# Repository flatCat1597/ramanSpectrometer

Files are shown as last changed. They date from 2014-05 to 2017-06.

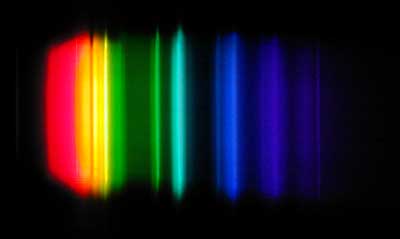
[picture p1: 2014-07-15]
info/images/youTube/video_1/images/Spectrum-hp-sodium.jpg

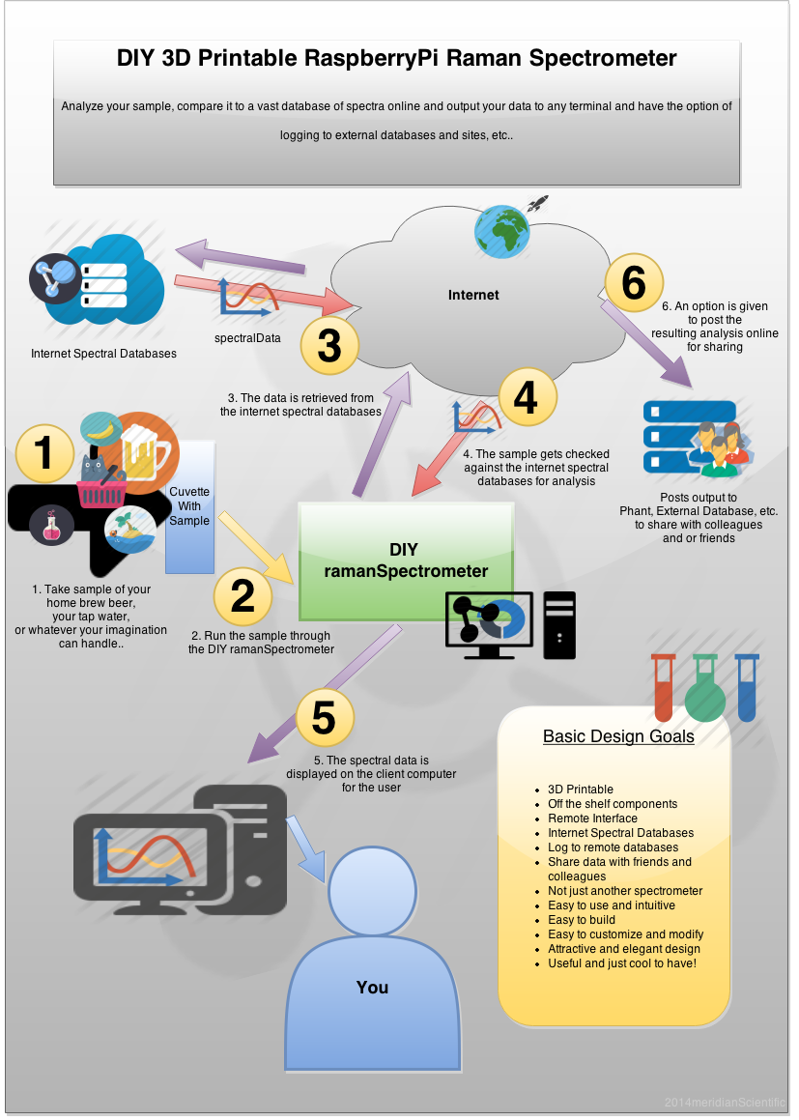
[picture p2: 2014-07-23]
info/images/diagrams/overview.png

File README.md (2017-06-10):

ramanPi
the DIY 3D Printable Raman Spectrometer

This repository will no longer contain ANY updates to the project.  The new repository at gitLab will have the latest files.  The github repo will NO LONGER be updated.  Please check the repository at https://gitlab.com/ramanPi before using any of the files here to build a ramanPi.

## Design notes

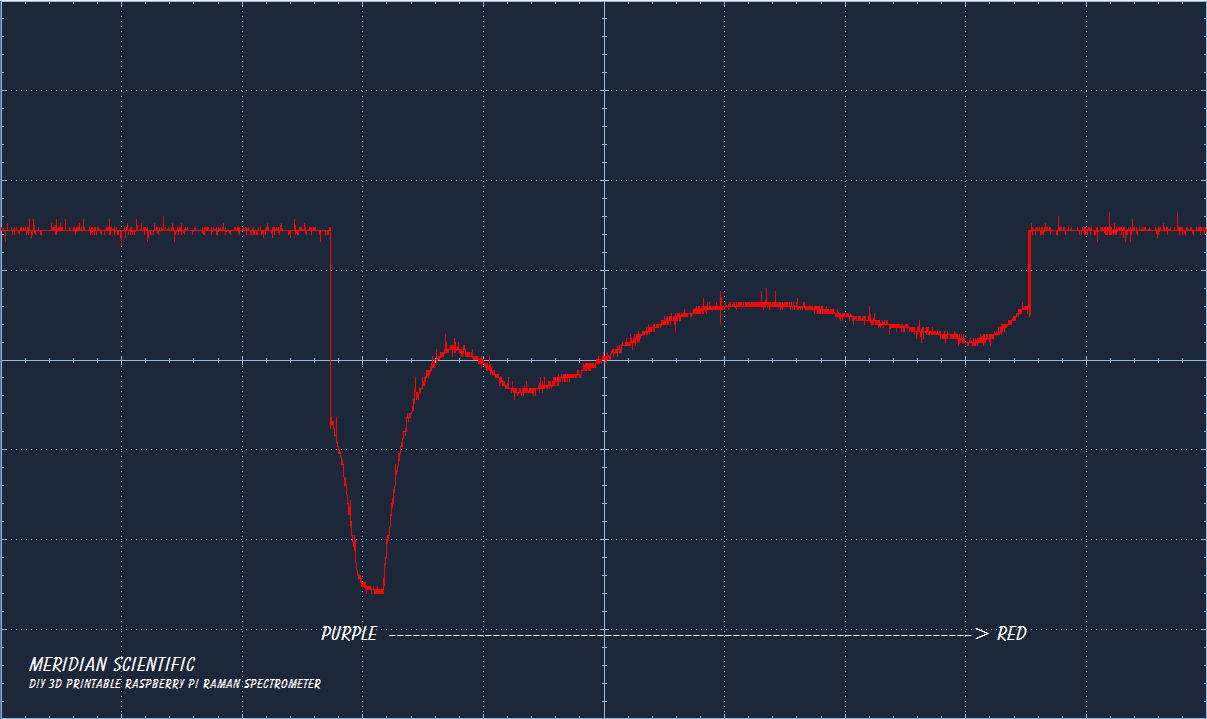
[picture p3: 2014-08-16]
info/images/images/spectra_flashlight_clearPurplePlastic.png

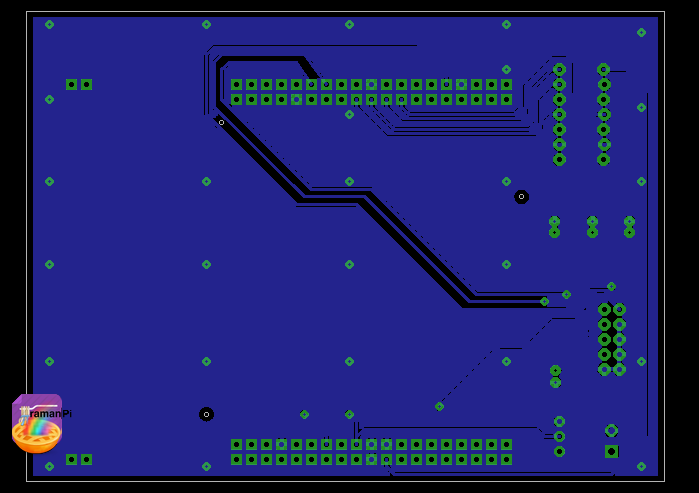
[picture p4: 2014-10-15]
hardware/electronics/imagingBoard/eagle/ramanPi_imagingBoard/images/ramanPi_imagingBoard_layout_bottom.png

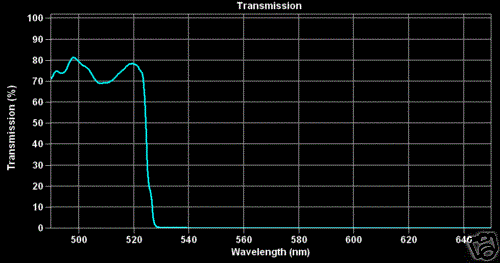
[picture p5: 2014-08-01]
info/images/diagrams/opticalFilter_522SP_5mmX40mmX2.4mm.GIF

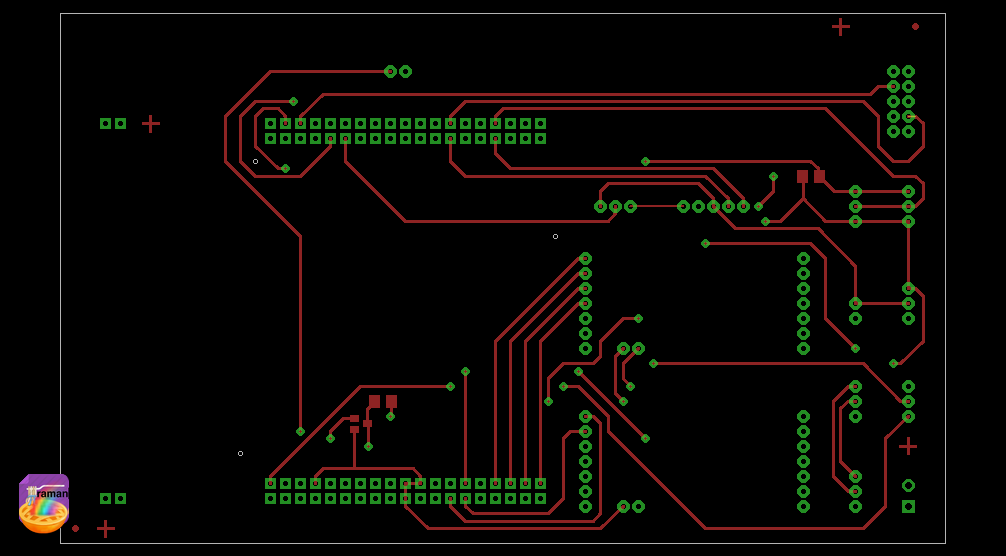
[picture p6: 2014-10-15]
hardware/electronics/controlBoard/eagle/ramanPi_controlBoard/images/ramanPi_controlBoard_layout_top.png

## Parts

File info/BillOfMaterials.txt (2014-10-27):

1x Raspberry Pi Model B+ 512MB RAM								(Adafruit 1914)	$39.95
3x ARM Nucleo Board STM32F4 STM32F401RE 512K 										$30
1x Tosbia TCD1304DG Linear CCD Array Detector 										$14.99
1800x grams or so of ABS black plastic filament 									$50-$90
1x Set of ramanPi PCB Kit (3x prototype boards, some solder and a long weekend)
1x 532nm 150mw Green Laser Module with Thermoelectric Cooling and TTL Modulated						$89.99
1x Edmund Optics 1200 Grooves/mm, 25mm Square, VIS Holographic Grating  Stock No. #43-216 				$135.00
1x Edmund Optics 20mm Dia x 80mm Focal Length, Spherical Mirror Stock No. #46-239 					$37.50
1x Edmund Optics 50mm Dia. x 100mm FL Protected Aluminum, Concave Mirror Stock No. #43-471  				$42.50
1x Edmund Optics 10µm x 3mm, Mounted, Precision Air Slit Stock No. #58-540 						$115.00
1x CVI 532nm bandpass interference filter one inch dia. # F10-532-4 							$30.00
1x Beam Splitter (preferably 532nm)											$48.00
1x 100x Microscope Objective Lens (Try not to pay more than $50 for one)						$11.99
1x Optical Filter 522SP, 5mm X 40mm X 2.4mm thick									$16.00
1x Optical Filter, 550LP, 10.1mm dia. X 3mm thick									$12.00
1x 1 Newport Pyrex First Surface Laser Mirror 1" Model# 10R08 ER1							$22.50
1x BitFenix Mini-ITX Tower Case Without Power Supply, Midnight Black BFC-PRO-300-KKXSK-RP					$69.99
1x Stereo 2.8W Class D Audio Amplifier - I2C Control AGC - TPA2016				(Adafruit 1712)	$9.95
1x Adafruit 12-Key Capacitive Touch Sensor Breakout - MPR121					(Adafruit 1982)	$7.95
1x BMP180 Barometric Pressure/Temperature/Altitude Sensor- 5V ready 				(Adafruit 1603)	$9.95
1x RGB Color Sensor with IR filter and White LED - TCS34725 					(Adafruit 1334)	$7.95
1x SI1145 Digital UV Index / IR / Visible Light Sensor						(Adafruit 1777)	$9.95
2x Photo Interrupter - GP1A57HRJ00F							(SparkFun SEN-09299)	$1.95
2x Photo Interrupter Breakout Board - GP1A57HRJ00F					(SparkFun BOB-09322)	$1.50
1x 10pcs OPTICAL GLASS CUVETTE CUVETTE CELL 10mm 3.5ml #U5B								$28.00
2x 2pcs DC 5V Stepper Motor + ULN2003 Driver Test Module Board 28BYJ-48 for Arduino					$5.48
2x 3103 3.6V 3.3A 12W TEC TEC1-03103 Thermoelectric Cooler Peltier 3V 2pcs						$12.99
1x Arduino Pro Mini 													$3.00
1x FTDI USB Controller 3.3V 5V Female Firmware Loader and Programmer Arduino						$11.99
1x NeoPixel Ring - 24 x WS2812 5050 RGB LED with Integrated Drivers				(Adafruit 1586) $$19.95
1x 2.2 inch 2.2" SPI TFT LCD Display module 240x320 ILI9341 51/AVR/STM32/ARM/PIC					$5.57
1x 1pcs KY-040 Rotary Encoder Module for Arduino AVR PIC								$0.99
1x Edimax EW-7811Un 150 Mbps Wireless 11n Nano Size USB Adapter 								$8.70
1x Ushoppingcart White Cotton Gloves Gloves, film, coins, CD/DVD, Handling Gloves (12pairs)					$10.76
1x Kinivo BTD-400 Bluetooth 4.0 USB adapter 											$7.99
1x Kimtech Science KimWipes Delicate Task Wipers 1-ply 280 count  (For the optics)						$5.91
1x Dynarex Black Nitrile Exam Gloves, Box/100  (More for the optics)								$9.98
1x Plastic Transfer Pipettes 3ml, Gradulated, Pack of 100  (For putting our sample in the cuvette)				$5.50
1x Glass Vials, 1 Dram, Pack of 12												$5.49
1x SD/MicroSD Memory Card (4 GB SDHC)												$5.49
1x Apevia ITX-AP250W 250W Flex ATX Power Supply											$35.35
1x M2.5 x 12 Metric Socket Head Cap Screw 2.5mm thread x 12mm length Qty 100						$11.50
1x Bag of 20x M4 16mm Socket Cap Screws												$7.10
1x SG90 9g Micro Servos For RC Airplane											$2.97
1x Dual H Bridge DC Stepper Motor Drive Controller Board Module Arduino L298N CY					$7.25
1x 5× 24-POSITION ATX POWER SUPPLY CONNECTOR VERTICAL PCB • AMP-DUAC • MINI FIT JR					$0.99
1x 1-Channel 5V Relay Expansion Board Module Low Level Triger for Arduino AVR PIC					$1.80
1x 10 PCS USB Type-A Female PCB Mount Socket Plug Connector Right Angle 4 Pin New					$1.49
1x 30PC 2 Pin Plug-in Screw Terminal Block 5.0mm Pitch Connector PCB Mount Panel					$4.36
1x 2S JST-XH 7.4V Connector Adapter Plug & Cable 10pcs EM#01								$3.42
1x (4x) 4S- 5 Pin JST-XH LiPo Balance Connectors w/ Pins								$5.60
1x Premium 0.5m 1.5Ft HDMI male to female panel mount extension Gold Head Cable							$3.98
1x Cable Matters Combo, 270 Degree Right and 90 Degree Left Vertical Flat HDMI Adapter						$7.99
1x 5 x 40 Pin DIP SIP IC Sockets Adaptor Solder Type - USA SELLER - Free Shipping					$4.99
1x D-Link Hi-Speed USB 2.0 7-Port Powered Hub (DUB-H7)										$24.99
2x YCS Basics 6 Inch USB 2.0 Mini B Male to Right Angle Mini B Female Extension Cable						$5.29
2x 1 foot mini usb cable													$7.00
1x Blue GPU CPU Heatsink Cooling Thermal Conductive Silicone Pad 100mmx100mmx1mm					$4.99
1x Nashua Aluminum Multi-Purpose Foil Tape, 3.2 mil Thick, 9 m Length, 48 mm Width					$9.64
1x Cast Acrylic Sheet, Transparent Gray, 12" x 12" x 0.118" Size							$5.25
10x 10-1000pcs WS2812B LED With Heatsink 5050 SMD RGB WS2811S IC Built-in 5V						$5.54
1x NEW Vktech 5pcs DS18b20 Waterproof Temperature Sensors Temperature Transmitter					$13.81
1x 30A Range Current Sensor Module ACS712 ACS712ELCTR-30A For Arduino Module D3						$4.92
1x Blank Arduino Shield Prototype Board											$7.20
1x 2x5 Pin IDC Ribbon Cable								(SparkFun PRT-08535)	$1.50
1x 10 Pcs 2.54mm 2x5 Pin 10 Pin Straight Male Shrouded PCB Box header IDC Socket					#3.99
1x Aspen Aerogel SPACELOFT Insulation Hydrophobic Mat, 10" x 14" Sample 5mm						$7.00
1x Car Vehicle 19mm 12V Blue LED Angel Eye Push Power Button Metal Switch Latching					$4.99
1x Neon gas ampoule, purity 99.999% element sample									$9.86
1x HIH-4030 Humidity Sensor Breakout							(SparkFun SEN-09569)	$16.95
10X 3S JST-XH Connector Adapter plug for 3 Cell 11.1v battery 4Pin male&female						$2.86
1x JST 2.0mm PH 2-Pin Connector with Wire x 20 Sets									$4.99
6x .01uf capacitor (smd 1206) - decoupling for imagingBoard/CCD								$0.05
1x 100Pcs MMBT2222 SOT-23 2N2222 SMD NPN Transistor									$0.99
1x Red LED for imagingBoard indicator											$0.25
1x Blue LED for imagingBoard indicator											$0.25
1x 1206 SMD/SMT Surface mount Resistors - 20pcs 10K									$1.00

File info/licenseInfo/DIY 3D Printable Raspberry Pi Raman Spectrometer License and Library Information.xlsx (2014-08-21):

This is a living document.. Information will be added and removed as appropriate.
Item | Link | Part Number | License Name | Link to License | Software | Link | License | Link
ST Microelectronics
ST STM32F401 Nucleo F401RE | STM32 Nucleo development board (http://www.st.com/web/catalog/tools/FM116/SC959/SS1532/LN1847/PF260000?icmp=nucleo-ipf_pron_pr-nucleo_feb2014&sc=nucleoF401RE-pr) | STM32F401RE | (Open Platform v3) | Open platform license agreement for STM32 Nucleo boards (http://www.st.com/st-web-ui/static/active/en/resource/legal/legal_agreement/license_agreement/open_platform_license_agreement_v3.pdf) | mBed SDK | http://mbed.org/handbook/mbed-SDK - Apache 2.0
BMP180 Barometric Pressure/Temperature/Altitude Sensor- 5V ready | https://www.adafruit.com/products/1603 | PID: 1603 | Creative Commons Attribution-ShareAlike 3.0 Unported (CC BY-SA 3.0) | http://creativecommons.org/licenses/by-sa/3.0/ | Philip Smith / library for BMP180 | http://mbed.org/users/harrypowers/code/BMP180/ | Contributor Agreement | https://mbed.org/contributor_agreement/
RGB Color Sensor with IR filter and White LED - TCS34725 | https://www.adafruit.com/products/1334 | PID: 1334 | Creative Commons Attribution-ShareAlike 3.0 Unported (CC BY-SA 3.0) | http://creativecommons.org/licenses/by-sa/3.0/ | Karl Maxwell / library for TCS3472_I2C | http://mbed.org/users/karlmaxwell67/code/TCS3472_I2C/ | Contributor Agreement | https://mbed.org/contributor_agreement/
SI1145 Digital UV Index / IR / Visible Light Sensor | https://www.adafruit.com/products/1777 | PID: 1777 | Creative Commons Attribution-ShareAlike 3.0 Unported (CC BY-SA 3.0) | http://creativecommons.org/licenses/by-sa/3.0/ | meridianScientific | https://github.com/flatcat1597 | GNU General Public License, version 2 | https://github.com/flatCat1597/ramanSpectrometer/blob/master/LICENShttps://github.com/flatCat1597/ramanSpectrometer/blob/master/LICENSE
Adafruit 12-Key Capacitive Touch Sensor Breakout - MPR121 | https://www.adafruit.com/products/1982 | PID: 1982 | Creative Commons Attribution-ShareAlike 3.0 Unported (CC BY-SA 3.0) | http://creativecommons.org/licenses/by-sa/3.0/ | Sam Grove / Freescale MPR121 | https://mbed.org/components/MPR121/ | Contributor Agreement | https://mbed.org/contributor_agreement/
Photo Interrupter Breakout Board - GP1A57HRJ00F | https://www.sparkfun.com/products/9322 | BOB-09322 | Creative Commons Attribution-ShareAlike 4.0 International (CC BY-SA 4.0) | https://creativecommons.org/licenses/by-sa/4.0/ | meridianScientific | https://github.com/flatcat1597 | GNU General Public License, version 2 | https://github.com/flatCat1597/ramanSpectrometer/blob/master/LICENShttps://github.com/flatCat1597/ramanSpectrometer/blob/master/LICENSE
Humidity Sensor Breakout - HIH-4030 | https://www.sparkfun.com/products/9569 | SEN-09569 | Creative Commons Attribution-ShareAlike 4.0 International (CC BY-SA 4.0) | https://creativecommons.org/licenses/by-sa/4.0/ | Simon Barker / library for HIH-4030 | http://mbed.org/users/simonbarker/code/HIH-4030/ | Contributor Agreement | https://mbed.org/contributor_agreement/
TFT_ILI9341 Color Display | http://www.eBay.com | TFT LCD | N/A ? |  | Peter Drescher / library for SPI_TFT_ILI9341 | http://mbed.org/users/dreschpe/code/SPI_TFT_ILI9341/ | Contributor Agreement | https://mbed.org/contributor_agreement/
DS18B20 Temperature Sensor | https://www.adafruit.com/products/381 | PID: 381 | N/A ? |  | Tony Mudd / library for MultipleDS18B20 | http://mbed.org/users/tonymudd/code/MultipleDS18B20/ | Contributor Agreement | https://mbed.org/contributor_agreement/
microchip / digilent
chipKit Uno32 | chipKit Uno32 (http://www.digilentinc.com/Products/Detail.cfm?Prod=CHIPKIT-UNO32) | Uno32 | Creative Commons Attribution-ShareAlike 3.0 Unported (CC BY-SA 3.0) | http://creativecommons.org/licenses/by-sa/3.0/ | MPIDE | http://chipkit.net/started/install-chipkit-software/
Arduino
Pro Mini | http://arduino.cc/en/Main/ArduinoBoardProMini | ProMini | Creative Commons Attribution-ShareAlike 3.0 Unported (CC BY-SA 3.0) | http://creativecommons.org/licenses/by-sa/3.0/ | Arduino IDE | http://arduino.cc/en/Main/Software
NeoPixel Ring - 24 x WS2812 5050 RGB LED with Integrated Drivers | https://www.adafruit.com/products/1586 | PID: 1586 | Creative Commons Attribution-ShareAlike 3.0 Unported (CC BY-SA 3.0) | http://creativecommons.org/licenses/by-sa/3.0/ | Adafruit NeoPixel library | https://github.com/adafruit/Adafruit_NeoPixel | GNU GENERAL PUBLIC LICENSE Version 3 | https://github.com/adafruit/Adafruit_NeoPixel/blob/master/COPYING
Breadboard-friendly RGB Smart NeoPixel - Sheet of 25 | https://www.adafruit.com/products/1558 | PID: 1558 | Creative Commons Attribution-ShareAlike 3.0 Unported (CC BY-SA 3.0) | http://creativecommons.org/licenses/by-sa/3.0/ | Adafruit NeoPixel library | https://github.com/adafruit/Adafruit_NeoPixel | GNU GENERAL PUBLIC LICENSE Version 3 | https://github.com/adafruit/Adafruit_NeoPixel/blob/master/COPYING
raspberryPi
raspberryPi Model B | http://www.raspberrypi.org/product/model-b/ | raspnerryPi | Attribution-ShareAlike 4.0 International (CC BY-SA 4.0) | https://creativecommons.org/licenses/by-sa/4.0/ | raspbian OS http://www.raspberrypi.org/downloads/ | http://raspbian.org/ | GNU General Public License, version 2 | http://www.gnu.org/licenses/gpl-2.0.html
Stereo 2.8W Class D Audio Amplifier - I2C Control AGC - TPA2016 | https://www.adafruit.com/products/1712 | PID: 1712 | Creative Commons Attribution-ShareAlike 3.0 Unported (CC BY-SA 3.0) | http://creativecommons.org/licenses/by-sa/3.0/ | n/a | n/a | n/a | n/a
 |  |  |  |  | Python | https://www.python.org/ | Python 2.7.7 license | https://www.python.org/download/releases/2.7.7/license
 |  |  |  |  | SciPy | http://www.scipy.org/ | SciPy license | http://www.scipy.org/scipylib/license.html
 |  |  |  |  | matPlotLib | http://matplotlib.org/ | based on the PSF license | http://matplotlib.org/users/license.html?highlight=license
 |  |  |  |  | numpy | http://www.numpy.org/ | Numpy license | http://www.numpy.org/license.html
 |  |  |  |  | Plot.py | http://plotpy.sourceforge.net/apidoc/index.html | none listed | n/a
 |  |  |  |  | Spectral Python | http://www.spectralpython.net/ | GNU General Public License | http://www.gnu.org/copyleft/gpl.html
 |  |  |  |  | pyVib2 | http://pyvib2.sourceforge.net/ | GNU General Public License, version 2 | http://pyvib2.sourceforge.net/license.shtml
 |  |  |  |  | spyder2 IDE | https://code.google.com/p/spyderlib/ | The MIT License (MIT) | http://opensource.org/licenses/mit-license.php

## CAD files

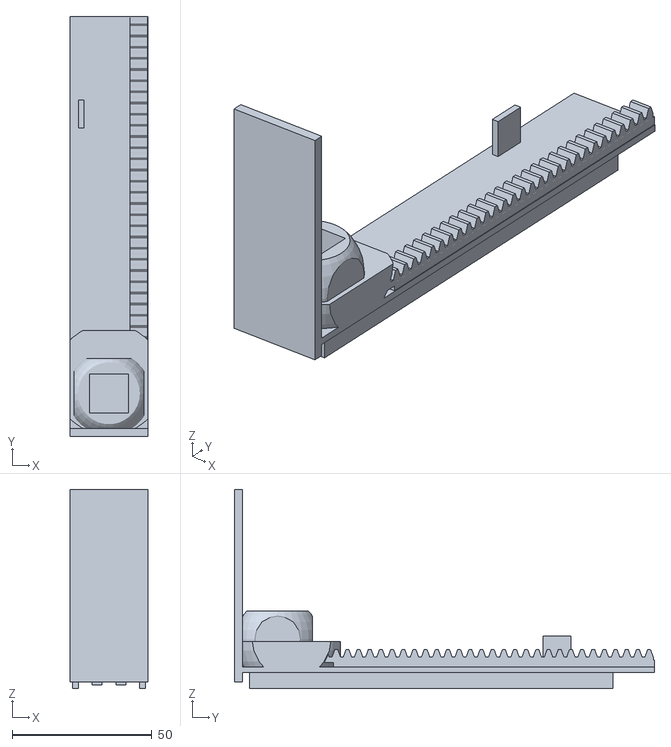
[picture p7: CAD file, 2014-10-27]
hardware/3dPrintable/files_stl/mechanical_device_cuvetteTrayAssembly.stl
28.0 x 150.5 x 71.2

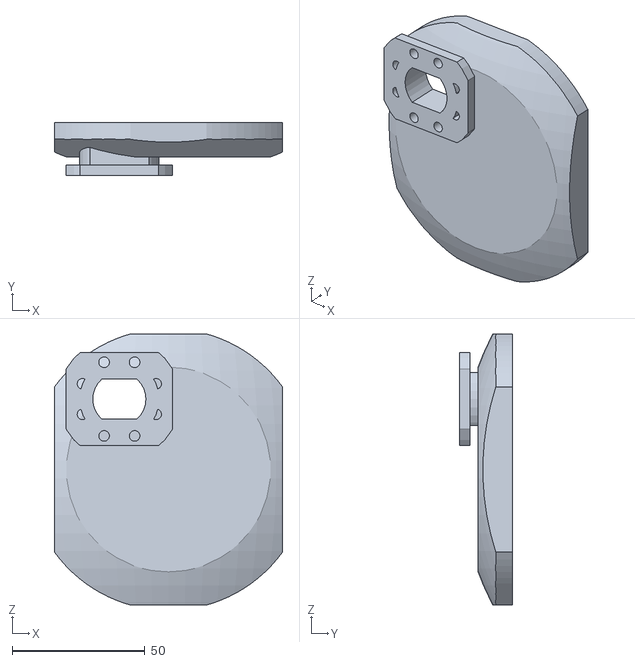
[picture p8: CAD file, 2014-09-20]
hardware/3dPrintable/files_stl/mechanical_device_filterSelectorAssembly_front.stl
86.0 x 20.0 x 102.0

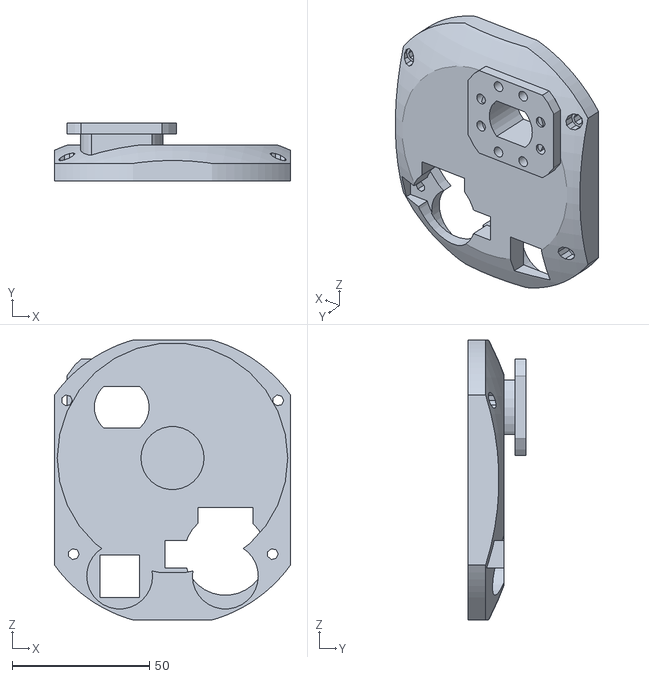
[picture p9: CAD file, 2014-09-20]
hardware/3dPrintable/files_stl/mechanical_device_filterSelectorAssembly_back.stl
86.0 x 21.0 x 102.0

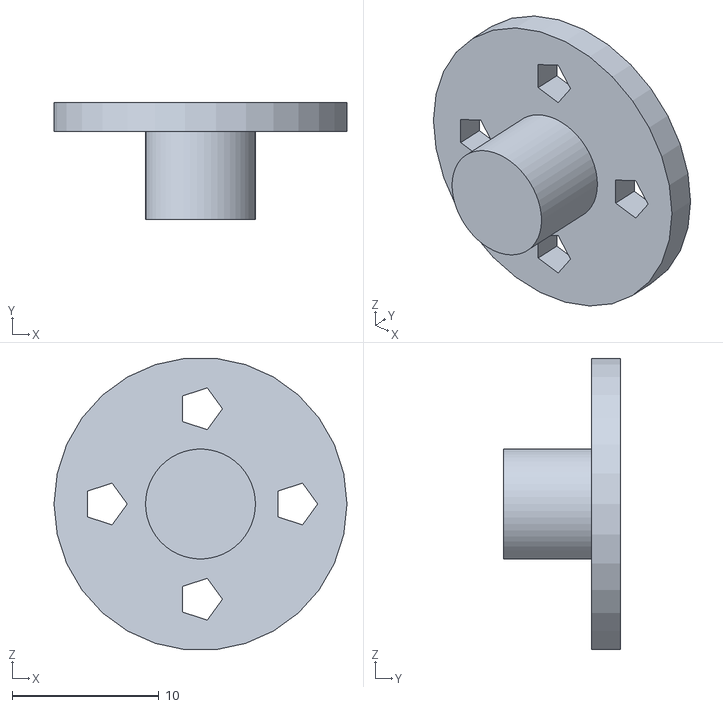
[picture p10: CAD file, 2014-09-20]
hardware/3dPrintable/files_stl/mechanical_device_filterSelectorAssembly_centerHub_Back.stl
20.0 x 8.00 x 19.9

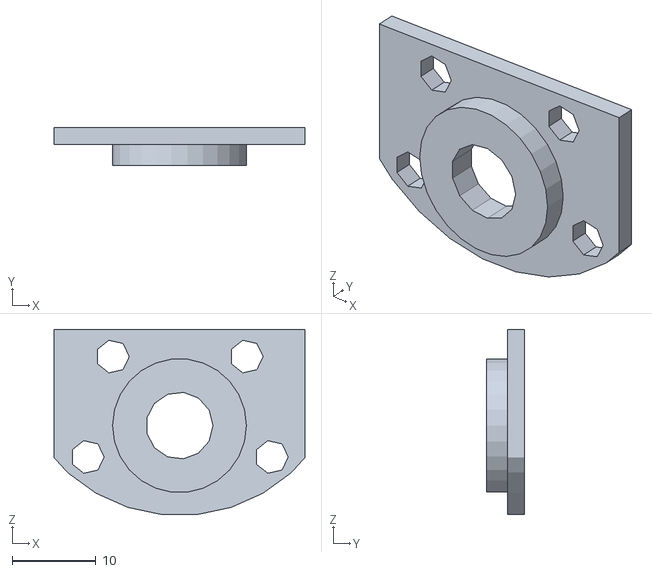
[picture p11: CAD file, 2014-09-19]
hardware/3dPrintable/files_stl/mechanical_device_filterSelectorAssembly_550nmSP_cover.stl
30.0 x 4.50 x 22.1

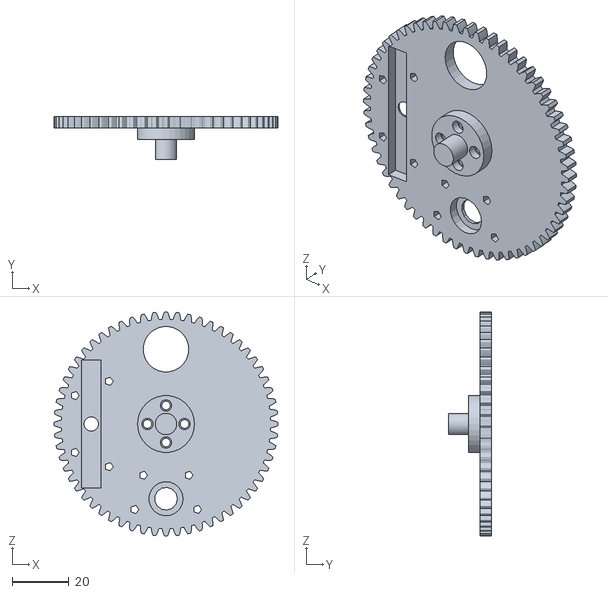
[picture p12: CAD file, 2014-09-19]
hardware/3dPrintable/files_stl/mechanical_device_filterSelectorAssembly_filterWheel.stl
78.7 x 15.0 x 78.7

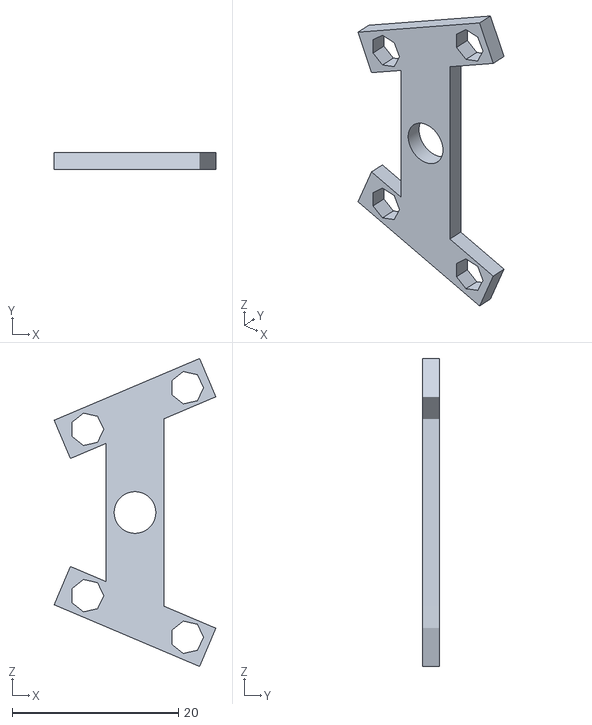
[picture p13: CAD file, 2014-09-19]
hardware/3dPrintable/files_stl/mechanical_device_filterSelectorAssembly_522nmSP_cover.stl
19.4 x 2.00 x 37.0

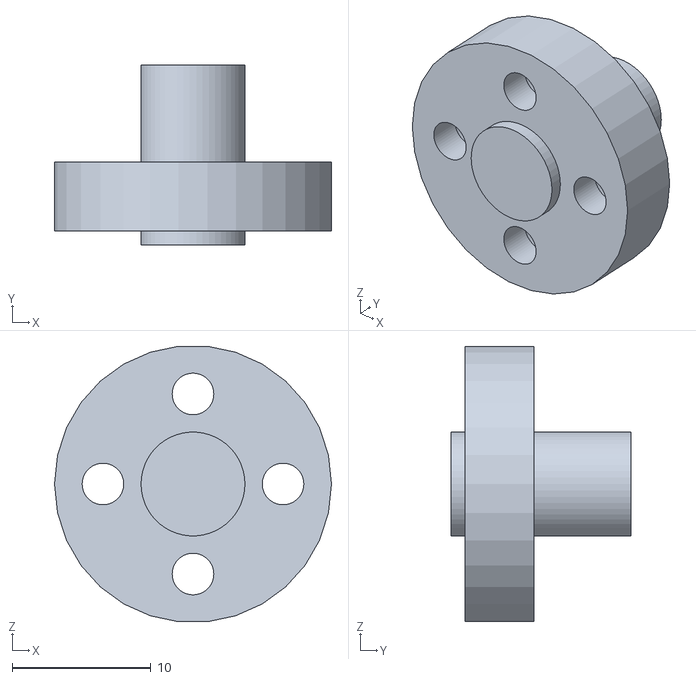
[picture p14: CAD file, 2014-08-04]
hardware/3dPrintable/files_stl/mechanical_device_filterSelectorAssembly_centerHub_Front.stl
20.0 x 13.0 x 19.9

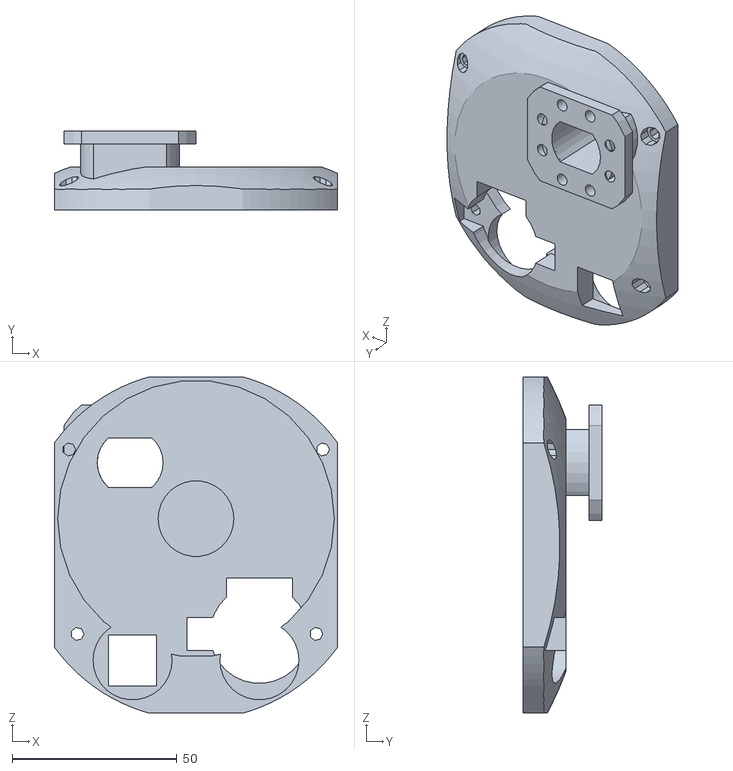
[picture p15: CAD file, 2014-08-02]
hardware/3dPrintable/files_stl/mechanical_device_filterSelectorAssembly_test2.stl
86.0 x 24.0 x 102.0

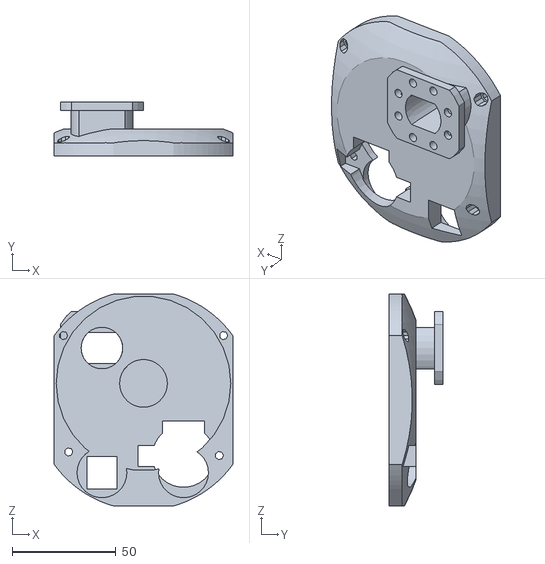
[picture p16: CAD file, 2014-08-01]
hardware/3dPrintable/files_stl/mechanical_device_filterSelectorAssembly.stl
86.0 x 26.0 x 102.0

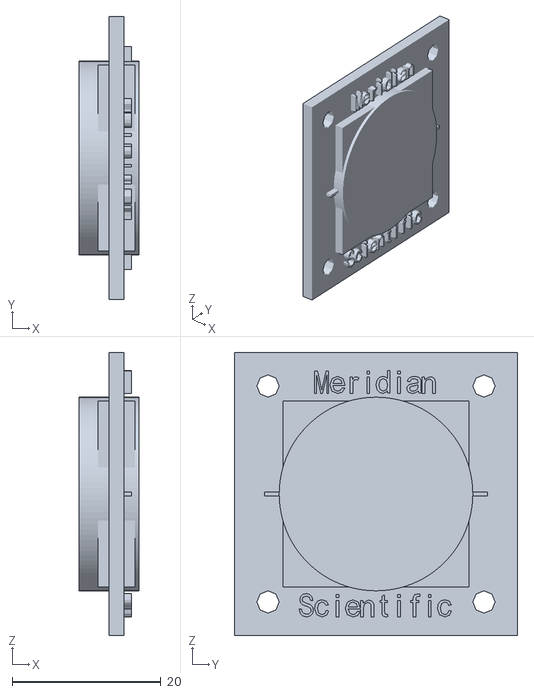
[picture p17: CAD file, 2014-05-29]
hardware/3dPrintable/files_stl/opticsMount_mirrorAssembly_rear.stl
8.00 x 38.0 x 38.0

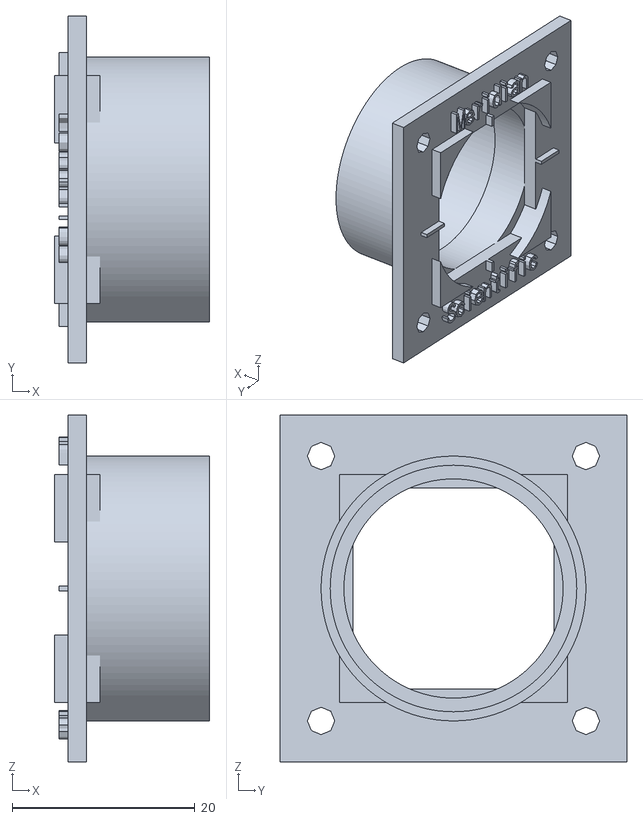
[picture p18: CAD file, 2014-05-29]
hardware/3dPrintable/files_stl/opticsMount_mirrorAssembly_front.stl
17.0 x 38.0 x 38.0

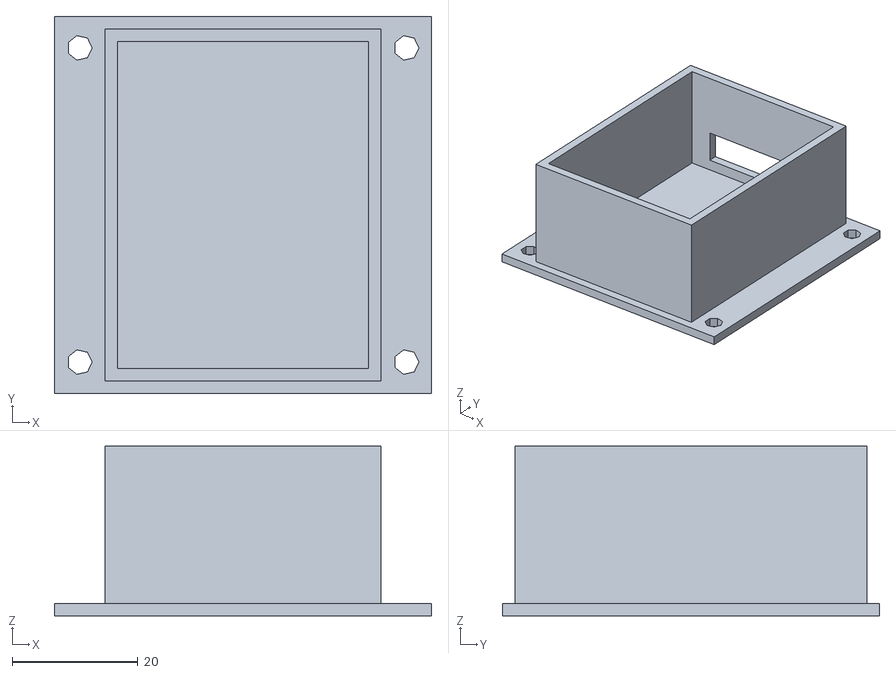
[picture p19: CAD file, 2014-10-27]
hardware/3dPrintable/files_stl/electronic_mount_relayBoard.stl
60.0 x 60.0 x 27.0

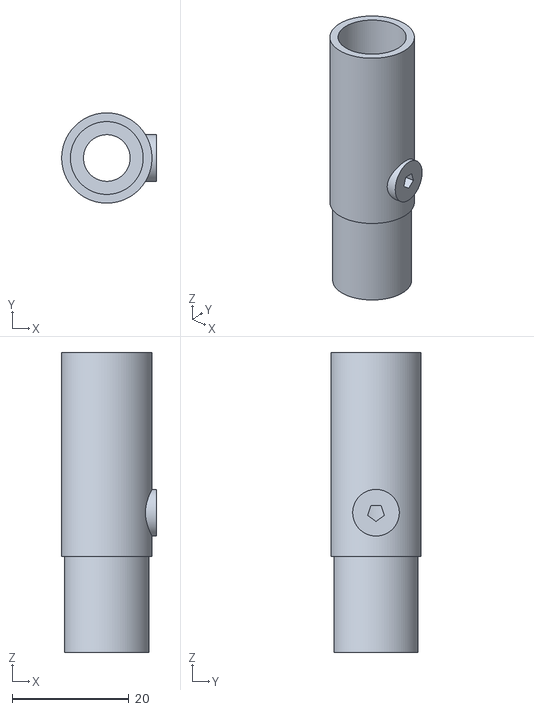
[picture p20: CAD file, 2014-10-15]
hardware/3dPrintable/files_stl/mechanical_device_cameoSharpieAdapter.stl
16.2 x 15.5 x 51.5

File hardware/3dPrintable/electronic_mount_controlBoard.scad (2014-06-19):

use <std_mechanical_object_tray.scad>
use <electronic_stNucleoF401RE.scad>

module edgeClips(){
	translate([0,0,6]){
		color([0.8,0.2,0.1]) cube(size=[3,25,12],center=true);
	}
	translate([3,0,4]){
		color([0.8,0.2,0.1]) cube(size=[8,15,9],center=true);
	}
	translate([1.5,0,13]){
		color([0.8,0.2,0.1]) cube(size=[6,25,2],center=true);
	}
}

module edgeClipPositions(){
	translate([-68,-36,0]){
		edgeClips();
	}
	translate([-68,35,0]){
		edgeClips();
	}
	translate([-15,-46,0]){
		rotate([0,0,90]){
			edgeClips();
		}
	}
	translate([-15,46,0]){
		rotate([0,0,270]){
			edgeClips();
		}
	}
	translate([45,-46,0]){
		rotate([0,0,90]){
			edgeClips();
		}
	}
	translate([45,46,0]){
		rotate([0,0,270]){
			edgeClips();
		}
	}
}

translate([-30,-4,10.25]){
	rotate([0,0,270]){
//		st_nucleo_F401RE();
	}
}

difference(){
	mainTray();
	translate([-32,-4,0]){
		cube(size=[55,70,4],center=true);
	}
	translate([32,-4,0]){
		cube(size=[55,70,4],center=true);
	}
}
edgeClipPositions();

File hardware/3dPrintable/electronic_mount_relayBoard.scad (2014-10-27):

//base
difference(){
	translate([0,0,-12.5]) cube(size=[60,60,2],center=true);
	translate([-26,-25,-12]) cylinder(r=2, h=5, center=true);
	translate([26,-25,-12]) cylinder(r=2, h=5, center=true);
	translate([-26,25,-12]) cylinder(r=2, h=5, center=true);
	translate([26,25,-12]) cylinder(r=2, h=5, center=true);
}
//box
difference(){
	cube(size=[44,56,27],center=true);
	translate([0,0,3]) cube(size=[40,52,26],center=true);
	translate([0,27,-4]) cube(size=[30,4,7],center=true);
}

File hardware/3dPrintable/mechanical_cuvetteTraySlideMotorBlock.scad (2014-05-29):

use <mechanical_rackAndPinion.scad>
use <electronic_photoInterrupter.scad>
use <arrow.scad>

module cuvetteTraySlideMotorBlock(){
	difference(){
		//mainBody
		color([.6,.2,.9]) cube(size=[70,60,20],center=true);
		//trayHole
		translate([0,0,3]) color([.73,.75,.95]) cube(size=[75,40,4],center=true);
		//railHoles
		translate([0,20,-1]) color([.73,.75,.95]) cube(size=[75,4,12],center=true);
		translate([0,-20,-1]) color([.73,.75,.95]) cube(size=[75,4,12],center=true);
		//rackHole
		translate([0,0,0]) color([.73,.75,.95]) cube(size=[75,15,10],center=true);
		//motorAndGearHole
		translate([0,10,-10]) color([.73,.75,.95]) cube(size=[27,45,15],center=true);
	}
	//verticalSupports
	translate([-32.5,0,-22]) color([.1,.5,.9]) cube(size=[5,30,30],center=true);
	translate([32.5,0,-22]) color([.1,.5,.9]) cube(size=[5,30,30],center=true);
	difference(){
		//stepperMountingPlate
		translate([0,3,-22]) color([.1,.5,.9]) cube(size=[65,5,30],center=true);
		//stepperShaftAndGearHole
		translate([0,3,-10]) rotate([90,0,0]) cylinder(h=10,r=13.75,center=true);
		//stepperMountingScrewHoles
		translate([17,3,-19]) rotate([90,0,0]) cylinder(h=10,r=2,center=true);
		translate([-17,3,-19]) rotate([90,0,0]) cylinder(h=10,r=2,center=true);
	}
	difference(){
		//mountingPlate
		translate([0,0,-36]) color([.1,.5,.9]) cube(size=[65,30,2],center=true);
		//wirePassSlot
		translate([0,12,-35])  cube(size=[10,20,5],center=true);
		//stepperMountingScrewHoles
		translate([17,-10,-35]) rotate([0,0,0]) cylinder(h=10,r=2,center=true);
		translate([-17,-10,-35]) rotate([0,0,0]) cylinder(h=10,r=2,center=true);
		translate([17,10,-35]) rotate([0,0,0]) cylinder(h=10,r=2,center=true);
		translate([-17,10,-35]) rotate([0,0,0]) cylinder(h=10,r=2,center=true);
	}
	translate([34,0,-20]){
		rotate([-90,0,0]){
			arrow();
		}
	}
	//photoInterrupter
//	translate([-38,-19,-6.5]) rotate([0,90,0])  photoInterrupter();
	difference(){	
		translate([-38,-19,-8]) cube(size=[6,22,18],center=true);
		translate([-39,-19,-5]) cube(size=[15,10,14],center=true);
		translate([-38,-19,-6]) cube(size=[4,20,17],center=true);
		translate([-38,-19,-15]) cube(size=[4,17,5],center=true);

		translate([-40,-23.5,-15]) cube(size=[11,17,10],center=true);
	}
//		translate([-38,-23,-16]) cube(size=[4,4,2],center=true);	
//		translate([-38,-15,-16]) cube(size=[4,4,2],center=true);	
}


translate([0,0,0]){
	cuvetteTraySlideMotorBlock();
}

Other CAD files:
hardware/3dPrintable/files_stl/trim_tftFaceplate_facia.stl
hardware/3dPrintable/files_stl/optics_module_surfaceMirror_bottom.stl
hardware/3dPrintable/files_stl/optics_module_surfaceMirror_top.stl
hardware/3dPrintable/mechanical_object_pinion.scad
hardware/3dPrintable/Write.scad
hardware/3dPrintable/arrow.scad
hardware/3dPrintable/combined_completeSystem.scad
hardware/3dPrintable/combined_electronic_mount_laser.scad
hardware/3dPrintable/combined_mechanical_device_laserShutter.scad
hardware/3dPrintable/combined_optics_module_surfaceMirror.scad
hardware/3dPrintable/combined_optoMechanical_objective-cuvette-displayAssembly.scad
hardware/3dPrintable/electronic_lcdDisplay.scad
hardware/3dPrintable/electronic_mount_laser_bottom.scad
hardware/3dPrintable/electronic_mount_laser_top.scad
hardware/3dPrintable/electronic_mount_raspberrPi.scad
hardware/3dPrintable/electronic_photoInterrupter.scad
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

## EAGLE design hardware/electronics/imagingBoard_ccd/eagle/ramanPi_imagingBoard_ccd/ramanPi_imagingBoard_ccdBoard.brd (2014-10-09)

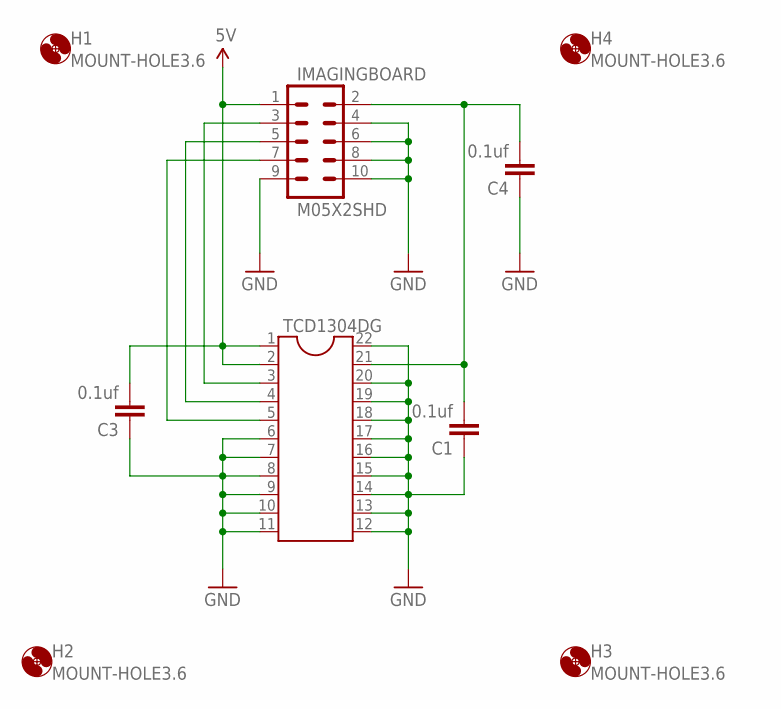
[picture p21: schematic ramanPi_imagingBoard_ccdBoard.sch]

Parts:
C1, C3, C4: 0.1uf; 1210
H1, H2, H3, H4: MOUNT-HOLE3.6; 3,6
IMAGINGBOARD: M05X2SHD; 2X5-SHROUDED
TCD1304DG: DIL22-4

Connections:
5V: C3.2, IMAGINGBOARD.1, TCD1304DG.1, TCD1304DG.2
GND: C1.1, C3.1, C4.1, IMAGINGBOARD.4, IMAGINGBOARD.6, IMAGINGBOARD.8, IMAGINGBOARD.9, IMAGINGBOARD.10, TCD1304DG.6, TCD1304DG.7, TCD1304DG.8, TCD1304DG.9, TCD1304DG.10, TCD1304DG.11, TCD1304DG.12, TCD1304DG.13, TCD1304DG.14, TCD1304DG.15, TCD1304DG.16, TCD1304DG.17, TCD1304DG.18, TCD1304DG.19, TCD1304DG.20, TCD1304DG.22
unnamed: C1.2, C4.2, IMAGINGBOARD.2, TCD1304DG.21
unnamed: IMAGINGBOARD.5, TCD1304DG.4
unnamed: IMAGINGBOARD.7, TCD1304DG.5
unnamed: IMAGINGBOARD.3, TCD1304DG.3

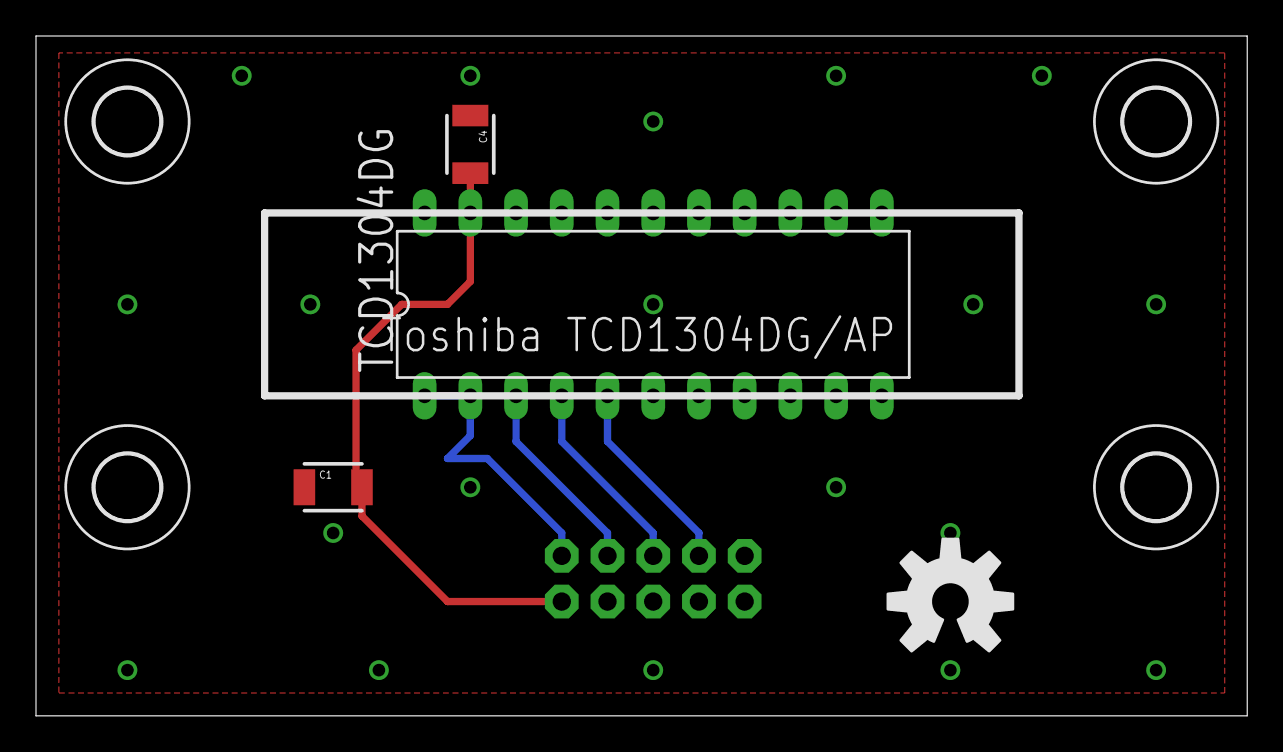
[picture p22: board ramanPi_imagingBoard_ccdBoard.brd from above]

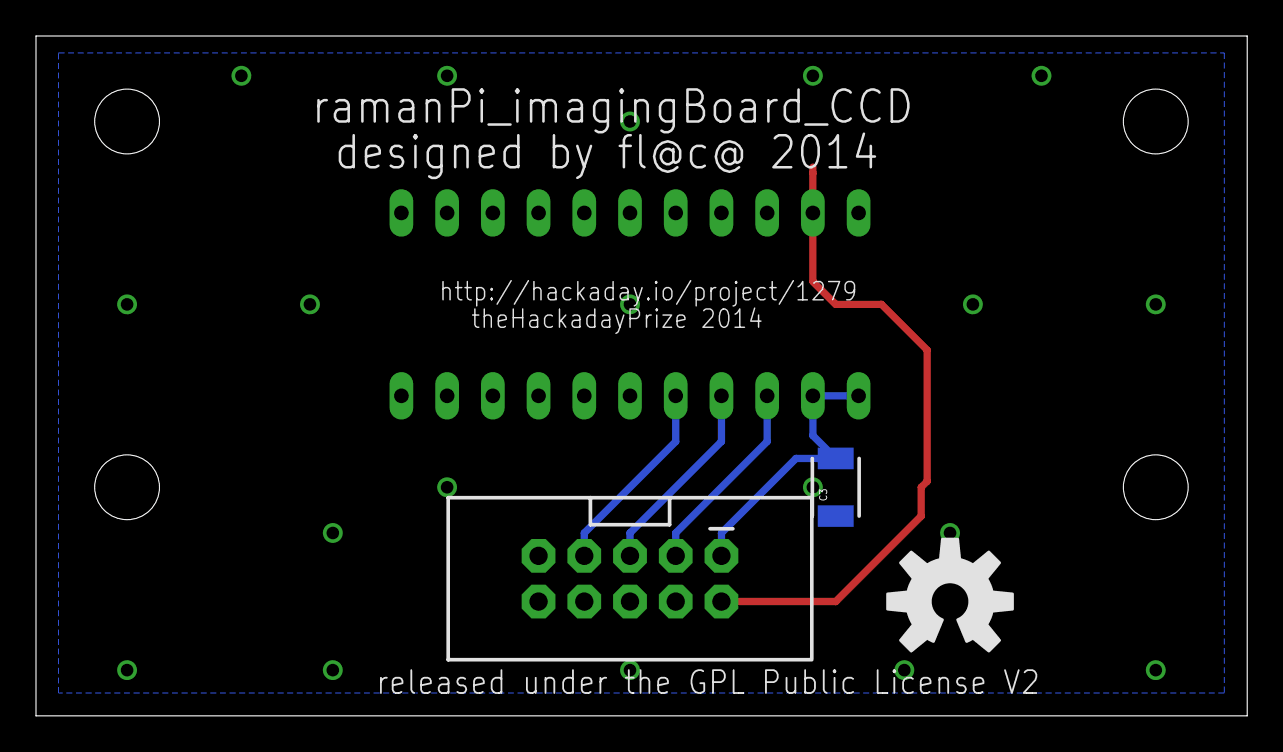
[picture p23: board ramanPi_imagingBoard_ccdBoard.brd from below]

Board: 2 copper layers, 67.3 x 37.8 mm, 11 parts (3 on the bottom side), 6 nets.

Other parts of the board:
U$1, U$2: OSHW-LOGO-L

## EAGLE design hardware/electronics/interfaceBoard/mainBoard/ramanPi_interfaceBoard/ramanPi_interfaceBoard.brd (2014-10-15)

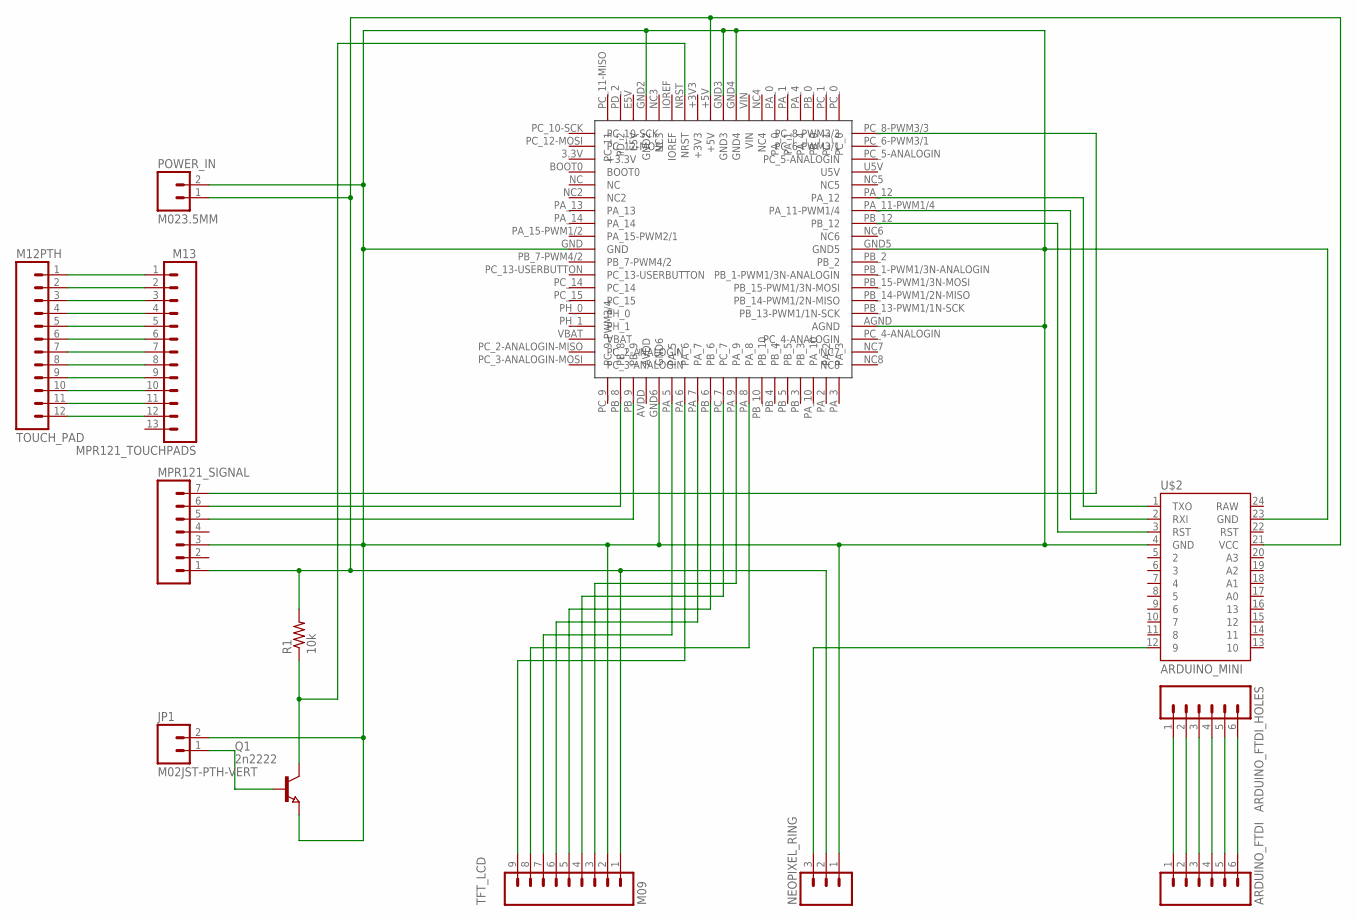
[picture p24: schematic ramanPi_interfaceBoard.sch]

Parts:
ARDUINO_FTDI: M06SIP; 1X06
ARDUINO_FTDI_HOLES: M06SIP; 1X06
JP1: M02JST-PTH-VERT; JST-2-PTH-VERT
MPR121_SIGNAL: M07; 1X07
MPR121_TOUCHPADS: M13; 1X13
NEOPIXEL_RING: M03JST-PTH-VERT; JST-3-PTH-VERT
POWER_IN: M023.5MM; SCREWTERMINAL-3.5MM-2
Q1: 2n2222; SOT23
R1: 10k; M1206
TFT_LCD: M09; 1X09
TOUCH_PAD: M12PTH; 1X12
U$1: STNUCLEOF401RE; F401-RE
U$2: ARDUINO_MINI

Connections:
+3.3V: U$1.3.3V (+3.3V)
+3V3: U$1.+3V3
+5V: MPR121_SIGNAL.1, NEOPIXEL_RING.2, POWER_IN.1, R1.2, TFT_LCD.1, U$1.+5V, U$2.21 (VCC)
AVDD: U$1.AVDD
E5V: U$1.E5V
GND: JP1.2, MPR121_SIGNAL.3, NEOPIXEL_RING.1, POWER_IN.2, Q1.2 (E), TFT_LCD.2, U$1.AGND, U$1.GND, U$1.GND2, U$1.GND3, U$1.GND4, U$1.GND5, U$1.GND6, U$2.4 (GND), U$2.23 (GND)
unnamed: MPR121_TOUCHPADS.1, TOUCH_PAD.1
unnamed: MPR121_TOUCHPADS.2, TOUCH_PAD.2
unnamed: MPR121_TOUCHPADS.3, TOUCH_PAD.3
unnamed: MPR121_TOUCHPADS.4, TOUCH_PAD.4
unnamed: MPR121_TOUCHPADS.5, TOUCH_PAD.5
unnamed: MPR121_TOUCHPADS.6, TOUCH_PAD.6
unnamed: MPR121_TOUCHPADS.7, TOUCH_PAD.7
unnamed: MPR121_TOUCHPADS.8, TOUCH_PAD.8
unnamed: MPR121_TOUCHPADS.9, TOUCH_PAD.9
unnamed: MPR121_TOUCHPADS.10, TOUCH_PAD.10
unnamed: MPR121_TOUCHPADS.11, TOUCH_PAD.11
unnamed: MPR121_TOUCHPADS.12, TOUCH_PAD.12
unnamed: NEOPIXEL_RING.3, U$2.12 (9)
unnamed: MPR121_SIGNAL.7, U$1.PC_8-PWM3/3
unnamed: MPR121_SIGNAL.5, U$1.PB_9
unnamed: MPR121_SIGNAL.6, U$1.PB_8
unnamed: ARDUINO_FTDI.1, ARDUINO_FTDI_HOLES.1
unnamed: ARDUINO_FTDI.2, ARDUINO_FTDI_HOLES.2
unnamed: ARDUINO_FTDI.3, ARDUINO_FTDI_HOLES.3
unnamed: ARDUINO_FTDI.4, ARDUINO_FTDI_HOLES.4
unnamed: ARDUINO_FTDI.5, ARDUINO_FTDI_HOLES.5
unnamed: ARDUINO_FTDI.6, ARDUINO_FTDI_HOLES.6
unnamed: TFT_LCD.3, U$1.PA_9
unnamed: U$1.PA_12, U$2.1 (TXO)
unnamed: U$1.PA_11-PWM1/4, U$2.2 (RXI)
unnamed: U$1.PB_12, U$2.3 (RST)
unnamed: TFT_LCD.4, U$1.PC_7
unnamed: TFT_LCD.5, U$1.PB_6
unnamed: TFT_LCD.6, U$1.PA_7
unnamed: TFT_LCD.7, U$1.PA_5
unnamed: TFT_LCD.8, U$1.PA_8
unnamed: TFT_LCD.9, U$1.PA_6
unnamed: Q1.3 (C), R1.1, U$1.NRST
unnamed: JP1.1, Q1.1 (B)
U5V: U$1.U5V
VBAT: U$1.VBAT
VIN: U$1.VIN

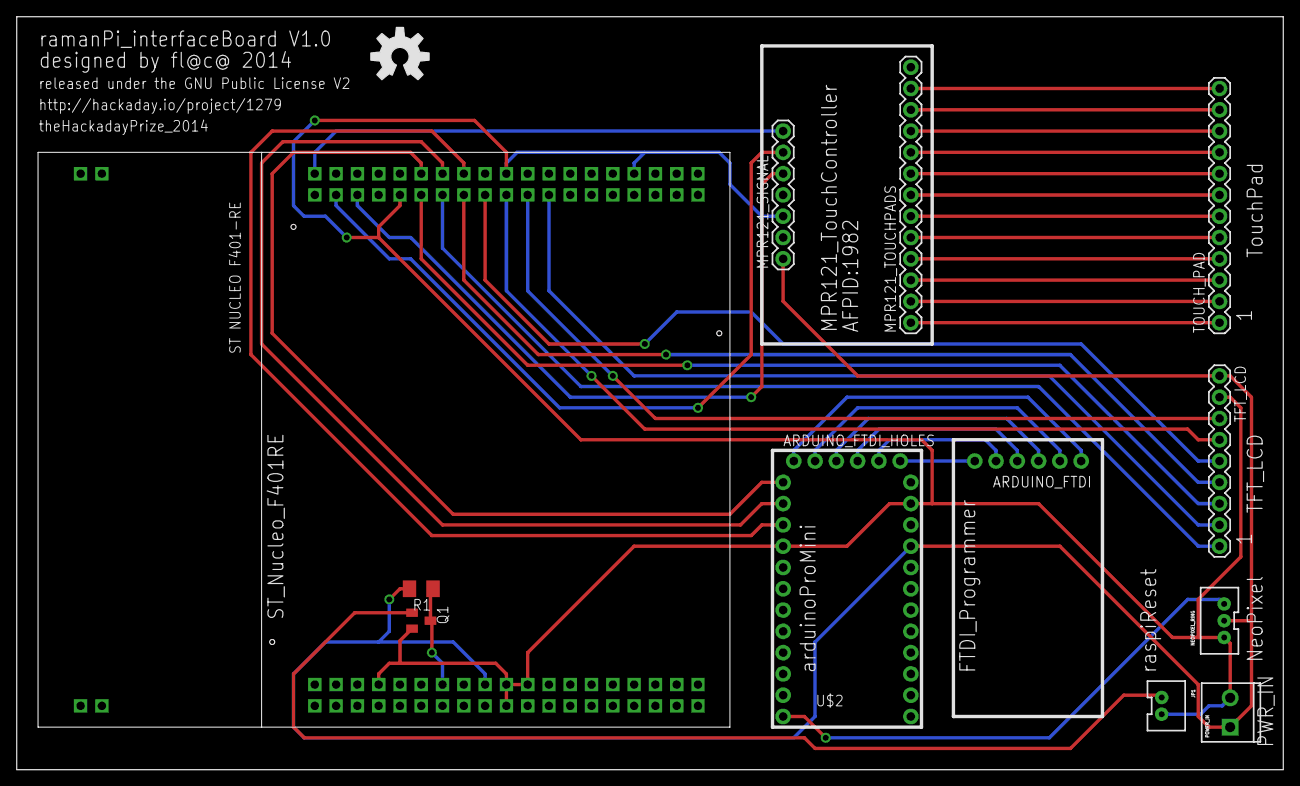
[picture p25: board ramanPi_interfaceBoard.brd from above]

Board: 2 copper layers, 151.1 x 89.8 mm, 14 parts (0 on the bottom side), 36 nets.

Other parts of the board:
U$3: OSHW-LOGO-L

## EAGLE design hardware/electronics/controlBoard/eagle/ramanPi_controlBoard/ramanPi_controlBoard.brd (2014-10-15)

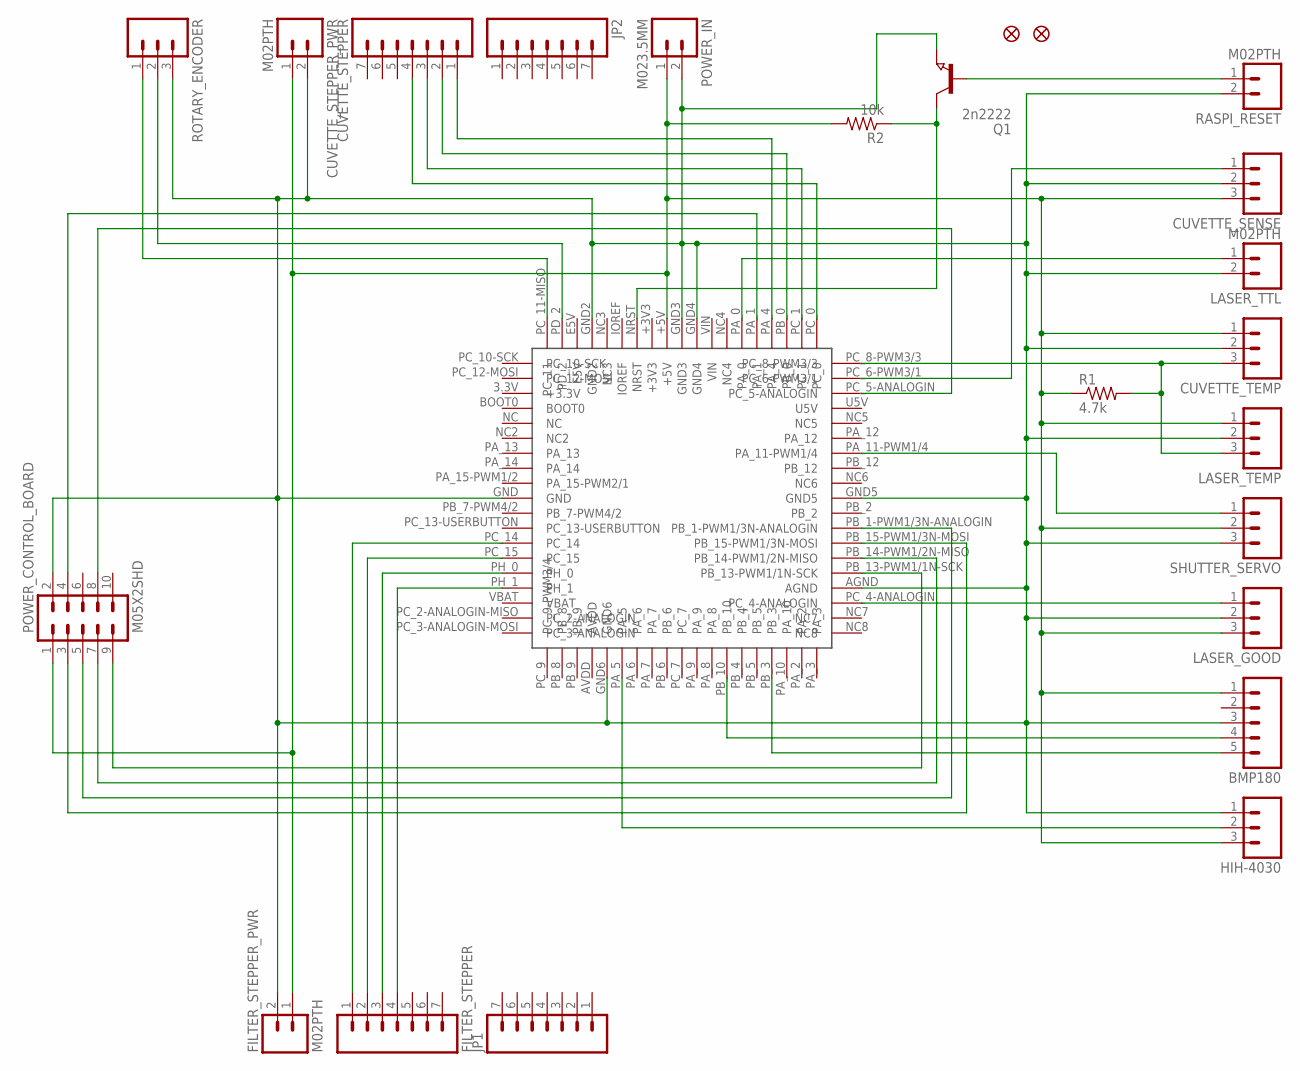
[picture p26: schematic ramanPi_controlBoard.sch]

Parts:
BMP180: M05PTH; 1X05
CUVETTE_SENSE: M03PTH; 1X03
CUVETTE_STEPPER: M07; 1X07
CUVETTE_STEPPER_PWR: M02PTH; 1X02
CUVETTE_TEMP: M03PTH; 1X03
FID1, FID2: FIDUCIAL1X2; FIDUCIAL-1X2
FILTER_STEPPER: M07; 1X07
FILTER_STEPPER_PWR: M02PTH; 1X02
HIH-4030: M03PTH; 1X03
JP1, JP2: M07; 1X07
LASER_GOOD: M03PTH; 1X03
LASER_TEMP: M03PTH; 1X03
LASER_TTL: M02PTH; 1X02
POWER_CONTROL_BOARD: M05X2SHD; 2X5-SHROUDED
POWER_IN: M023.5MM; SCREWTERMINAL-3.5MM-2
Q1: 2n2222; SOT23
R1: 4.7k; M1206
R2: 10k; M1206
RASPI_RESET: M02PTH; 1X02
ROTARY_ENCODER: M03PTH; 1X03
SHUTTER_SERVO: M03PTH; 1X03
U$1: STNUCLEOF401RE; F401-RE

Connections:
+3.3V: U$1.3.3V (+3.3V)
+3V3: U$1.+3V3
+5V: BMP180.1, CUVETTE_SENSE.3, CUVETTE_STEPPER_PWR.1, CUVETTE_TEMP.1, FILTER_STEPPER_PWR.1, HIH-4030.3, LASER_GOOD.3, LASER_TEMP.1, POWER_CONTROL_BOARD.1, POWER_IN.1, R1.1, R2.2, SHUTTER_SERVO.2, U$1.+5V
AVDD: U$1.AVDD
E5V: U$1.E5V
GROUND: BMP180.3, CUVETTE_SENSE.2, CUVETTE_STEPPER_PWR.2, CUVETTE_TEMP.2, FILTER_STEPPER_PWR.2, HIH-4030.1, LASER_GOOD.2, LASER_TEMP.2, LASER_TTL.2, POWER_CONTROL_BOARD.2, POWER_IN.2, Q1.2 (E), RASPI_RESET.2, ROTARY_ENCODER.3, SHUTTER_SERVO.3, U$1.AGND, U$1.GND, U$1.GND2, U$1.GND3, U$1.GND4, U$1.GND5, U$1.GND6
unnamed: BMP180.5, U$1.PB_3
unnamed: BMP180.4, U$1.PB_10
unnamed: CUVETTE_SENSE.1, U$1.PC_6-PWM3/1
unnamed: HIH-4030.2, U$1.PA_5
unnamed: CUVETTE_TEMP.3, LASER_TEMP.3, R1.2, U$1.PC_8-PWM3/3
unnamed: POWER_CONTROL_BOARD.4, U$1.PA_1
unnamed: LASER_TTL.1, U$1.PA_0
unnamed: POWER_CONTROL_BOARD.3, U$1.PB_15-PWM1/3N-MOSI
unnamed: POWER_CONTROL_BOARD.5, U$1.PB_1-PWM1/3N-ANALOG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
unnamed: POWER_CONTROL_BOARD.7, U$1.PB_14-PWM1/2N-MISO
unnamed: POWER_CONTROL_BOARD.9, U$1.PB_13-PWM1/1N-SCK
unnamed: POWER_CONTROL_BOARD.8, U$1.PC_5-ANALOGIN
unnamed: SHUTTER_SERVO.1, U$1.PA_11-PWM1/4
unnamed: LASER_GOOD.1, U$1.PC_4-ANALOGIN
unnamed: FILTER_STEPPER.1, U$1.PC_14
unnamed: FILTER_STEPPER.2, U$1.PC_15
unnamed: FILTER_STEPPER.3, U$1.PH_0
unnamed: FILTER_STEPPER.4, U$1.PH_1
unnamed: CUVETTE_STEPPER.1, U$1.PA_4
unnamed: CUVETTE_STEPPER.2, U$1.PB_0
unnamed: CUVETTE_STEPPER.3, U$1.PC_1
unnamed: CUVETTE_STEPPER.4, U$1.PC_0
unnamed: ROTARY_ENCODER.1, U$1.PC_11-MISO (PC_11)
unnamed: ROTARY_ENCODER.2, U$1.PD_2
unnamed: Q1.3 (C), R2.1, U$1.NRST
unnamed: Q1.1 (B), RASPI_RESET.1
U5V: U$1.U5V
VBAT: U$1.VBAT
VIN: U$1.VIN

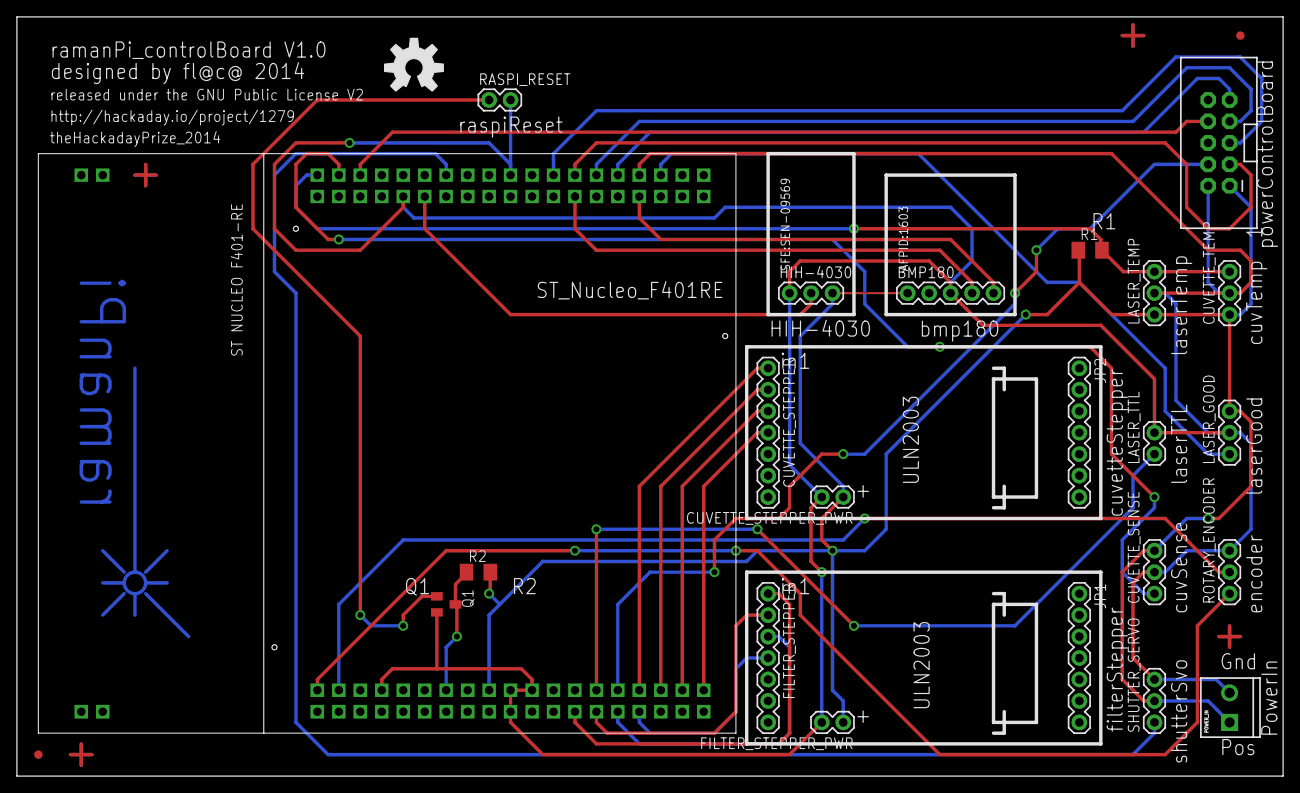
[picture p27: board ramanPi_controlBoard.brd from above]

Board: 2 copper layers, 149.8 x 89.8 mm, 25 parts (0 on the bottom side), 28 nets.

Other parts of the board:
U$2: OSHW-LOGO-L

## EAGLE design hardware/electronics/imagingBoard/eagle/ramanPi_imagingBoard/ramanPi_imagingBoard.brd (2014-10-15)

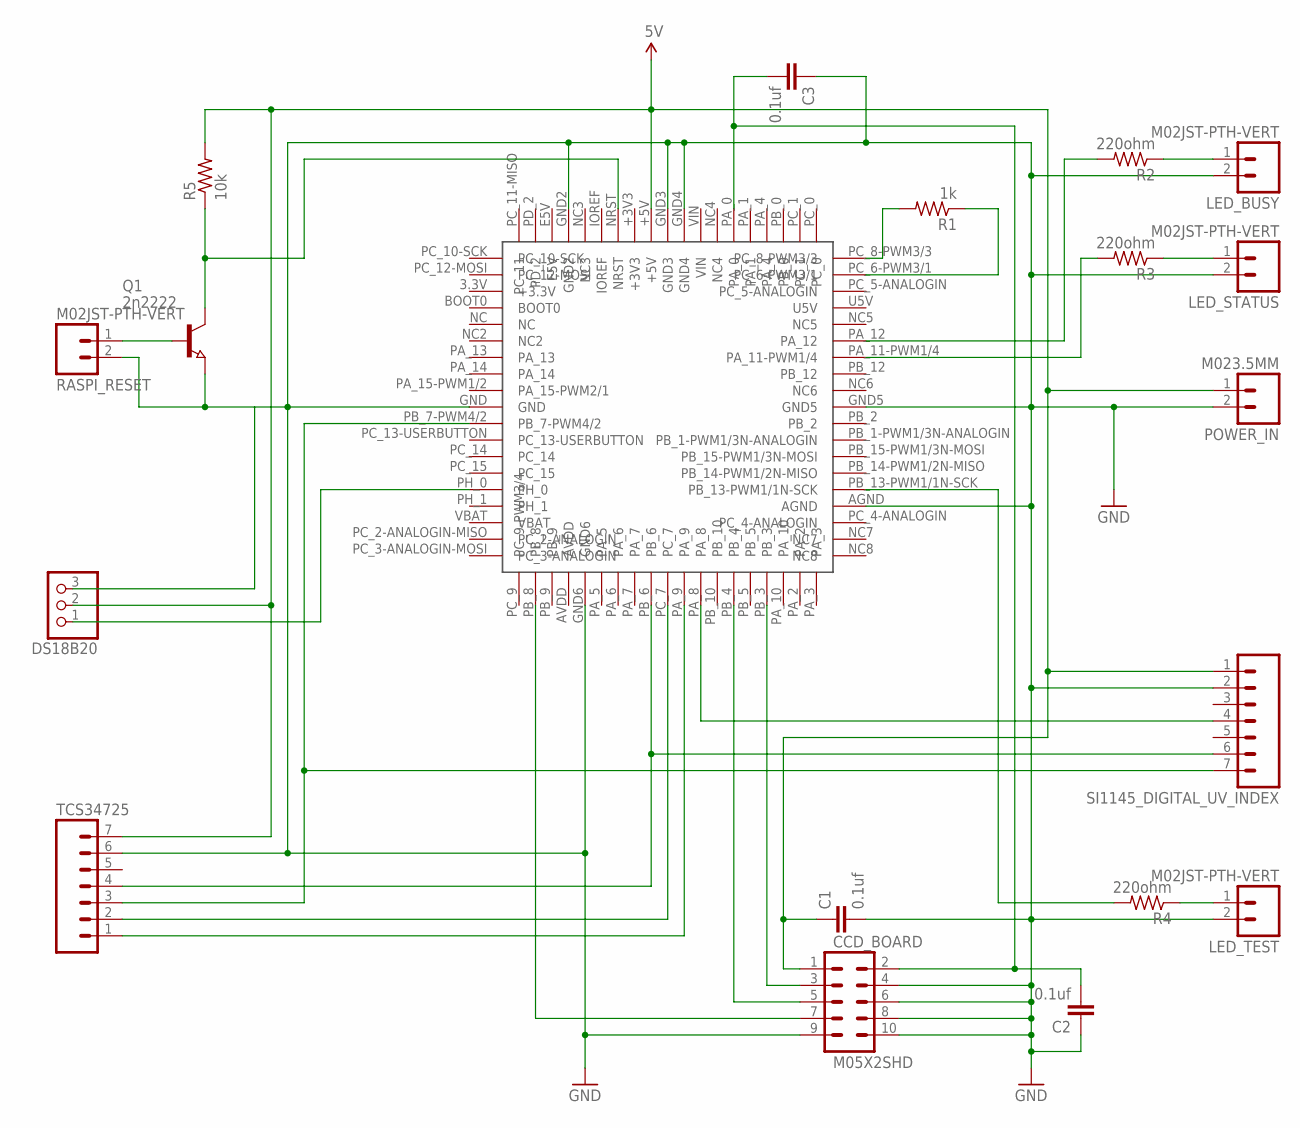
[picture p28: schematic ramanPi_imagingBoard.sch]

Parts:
C1, C2, C3: 0.1uf; 1210
CCD_BOARD: M05X2SHD; 2X5-SHROUDED
DS18B20: PINHD-1X3; 1X03
LED_BUSY: M02JST-PTH-VERT; JST-2-PTH-VERT
LED_STATUS: M02JST-PTH-VERT; JST-2-PTH-VERT
LED_TEST: M02JST-PTH-VERT; JST-2-PTH-VERT
POWER_IN: M023.5MM; SCREWTERMINAL-3.5MM-2
Q1: 2n2222; SOT23
R1: 1k; M1206
R2, R3, R4: 220ohm; M1206
R5: 10k; M1206
RASPI_RESET: M02JST-PTH-VERT; JST-2-PTH-VERT
SI1145_DIGITAL_UV_INDEX: M07LOCK; 1X07_LOCK
TCS34725: M07; 1X07
U$1: STNUCLEOF401RE; F401-RE

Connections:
5V: C1.1, CCD_BOARD.1, DS18B20.2, POWER_IN.1, R5.2, SI1145_DIGITAL_UV_INDEX.1, TCS34725.7, U$1.+5V
+3.3V: U$1.3.3V (+3.3V)
+3V3: U$1.+3V3
AVDD: U$1.AVDD
E5V: U$1.E5V
GND: C1.2, C2.1, C3.1, CCD_BOARD.4, CCD_BOARD.6, CCD_BOARD.8, CCD_BOARD.9, CCD_BOARD.10, DS18B20.3, LED_BUSY.2, LED_STATUS.2, LED_TEST.2, POWER_IN.2, Q1.2 (E), RASPI_RESET.2, SI1145_DIGITAL_UV_INDEX.2, TCS34725.6, U$1.AGND, U$1.GND, U$1.GND2, U$1.GND3, U$1.GND4, U$1.GND5, U$1.GND6
unnamed: CCD_BOARD.7, U$1.PB_8
unnamed: CCD_BOARD.5, U$1.PB_4
unnamed: Q1.1 (B), RASPI_RESET.1
unnamed: R1.2, U$1.PC_8-PWM3/3
unnamed: R1.1, U$1.PC_6-PWM3/1
unnamed: DS18B20.1, U$1.PH_0
unnamed: SI1145_DIGITAL_UV_INDEX.7, TCS34725.3, U$1.PB_7-PWM4/2
unnamed: SI1145_DIGITAL_UV_INDEX.6, TCS34725.4, U$1.PB_6
unnamed: C2.2, C3.2, CCD_BOARD.2, U$1.PA_0
unnamed: SI1145_DIGITAL_UV_INDEX.4, U$1.PA_8
unnamed: TCS34725.2, U$1.PC_7
unnamed: TCS34725.1, U$1.PA_9
unnamed: LED_BUSY.1, R2.1
unnamed: LED_STATUS.1, R3.1
unnamed: LED_TEST.1, R4.1
unnamed: R2.2, U$1.PA_12
unnamed: R3.2, U$1.PA_11-PWM1/4
unnamed: R4.2, U$1.PB_13-PWM1/1N-SCK
unnamed: Q1.3 (C), R5.1, U$1.NRST
unnamed: CCD_BOARD.3, U$1.PB_3
U5V: U$1.U5V
VBAT: U$1.VBAT
VIN: U$1.VIN

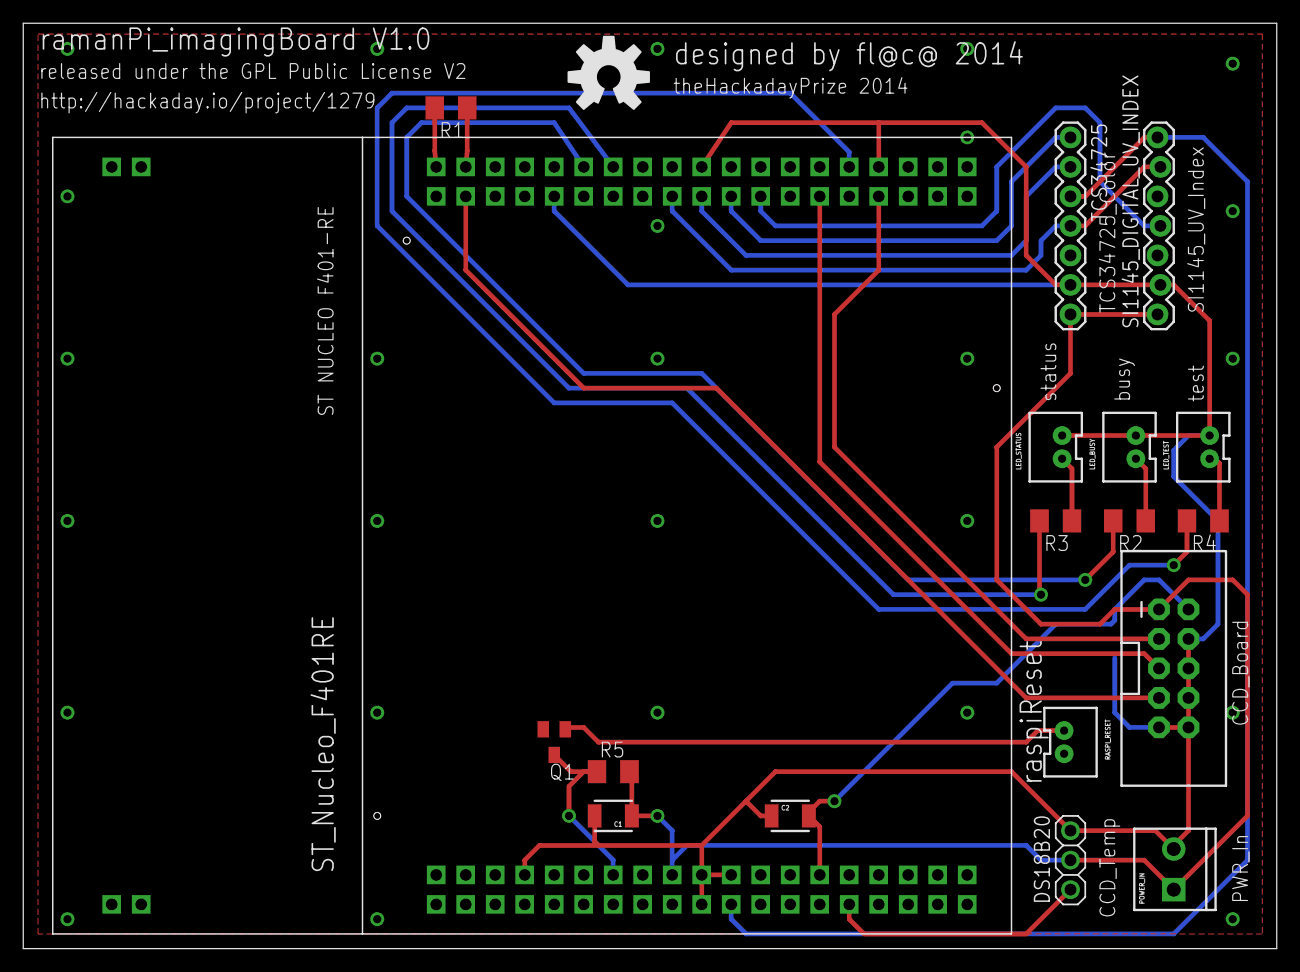
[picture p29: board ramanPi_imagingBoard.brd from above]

Board: 2 copper layers, 107.9 x 79.7 mm, 20 parts (1 on the bottom side), 22 nets.

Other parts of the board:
U$2: OSHW-LOGO-L

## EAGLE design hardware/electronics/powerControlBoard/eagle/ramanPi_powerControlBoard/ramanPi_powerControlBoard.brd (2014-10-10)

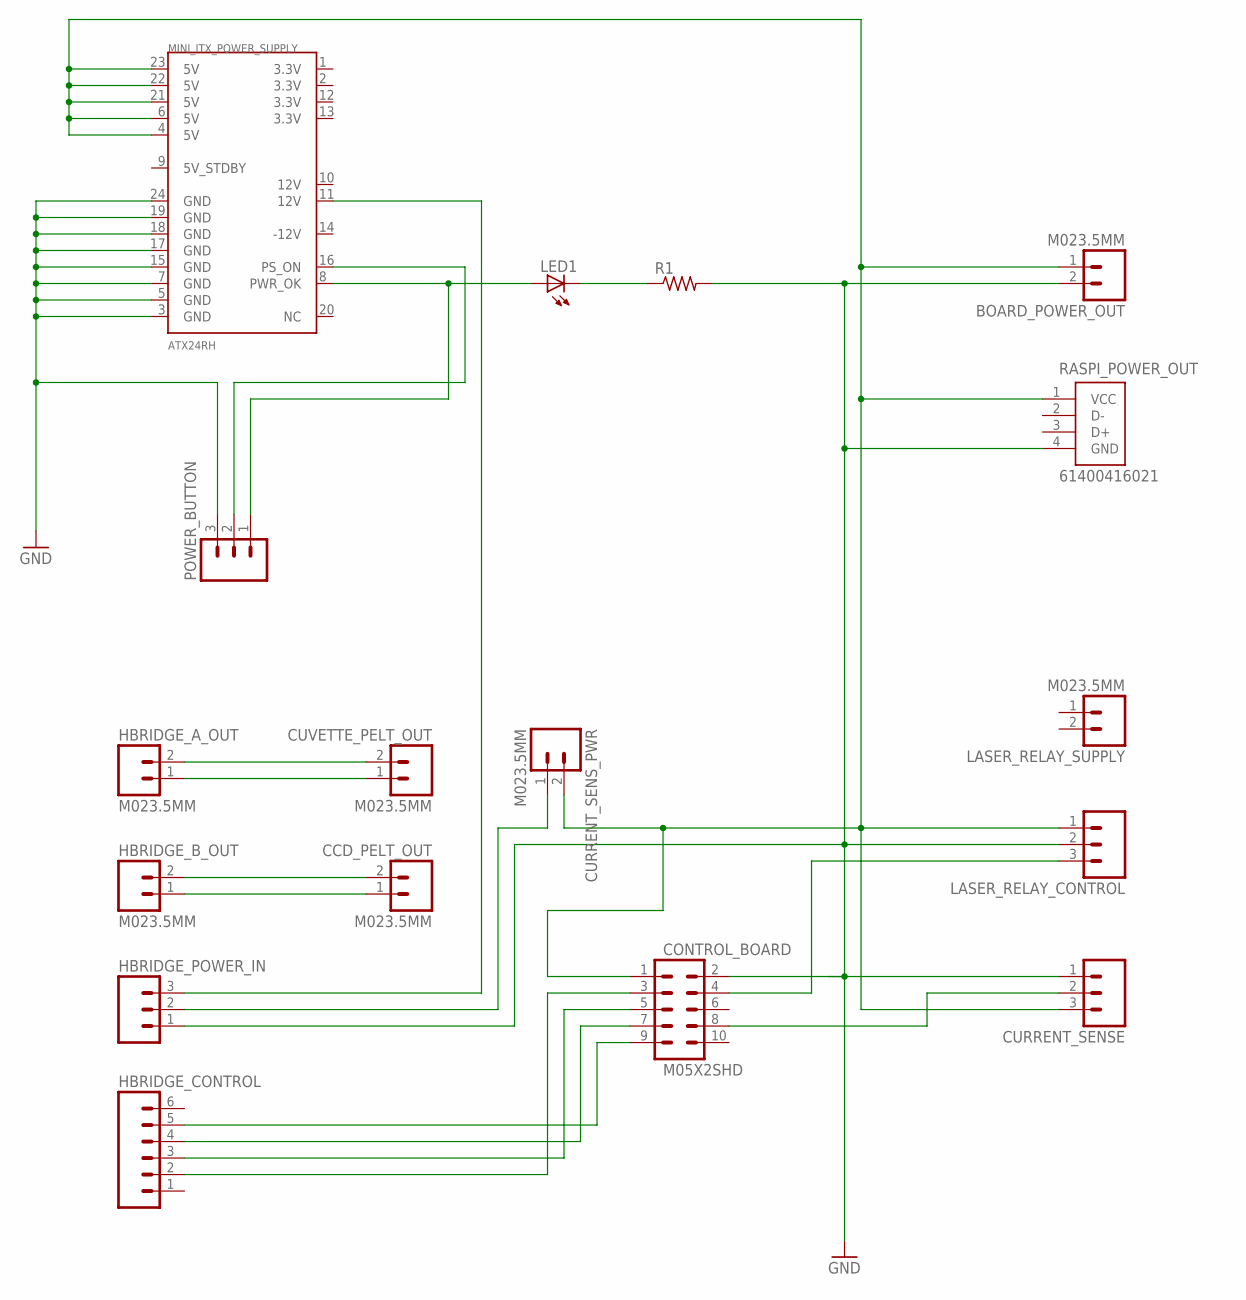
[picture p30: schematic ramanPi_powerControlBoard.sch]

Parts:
BOARD_POWER_OUT: M023.5MM; SCREWTERMINAL-3.5MM-2
CCD_PELT_OUT: M023.5MM; SCREWTERMINAL-3.5MM-2
CONTROL_BOARD: M05X2SHD; 2X5-SHROUDED
CURRENT_SENSE: M03PTH; 1X03
CURRENT_SENS_PWR: M023.5MM; SCREWTERMINAL-3.5MM-2
CUVETTE_PELT_OUT: M023.5MM; SCREWTERMINAL-3.5MM-2
HBRIDGE_A_OUT: M023.5MM; SCREWTERMINAL-3.5MM-2
HBRIDGE_B_OUT: M023.5MM; SCREWTERMINAL-3.5MM-2
HBRIDGE_CONTROL: M06SIP; 1X06
HBRIDGE_POWER_IN: M03SCREW; SCREWTERMINAL-3.5MM-3
LASER_RELAY_CONTROL: M03PTH; 1X03
LASER_RELAY_SUPPLY: M023.5MM; SCREWTERMINAL-3.5MM-2
LED1: LED5MM
MINI_ITX_POWER_SUPPLY: ATX24RH; ATX24_RIGHT_ANGLE
POWER_BUTTON: M03JST-PTH-VERT; JST-3-PTH-VERT
R1: R-US_M1206; M1206
RASPI_POWER_OUT: 61400416021

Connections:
GND: BOARD_POWER_OUT.2, CONTROL_BOARD.2, CURRENT_SENSE.1, HBRIDGE_POWER_IN.1, LASER_RELAY_CONTROL.2, MINI_ITX_POWER_SUPPLY.3 (GND), MINI_ITX_POWER_SUPPLY.5 (GND), MINI_ITX_POWER_SUPPLY.7 (GND), MINI_ITX_POWER_SUPPLY.15 (GND), MINI_ITX_POWER_SUPPLY.17 (GND), MINI_ITX_POWER_SUPPLY.18 (GND), MINI_ITX_POWER_SUPPLY.19 (GND), MINI_ITX_POWER_SUPPLY.24 (GND), POWER_BUTTON.3, R1.2, RASPI_POWER_OUT.4 (GND)
unnamed: CONTROL_BOARD.4, LASER_RELAY_CONTROL.3
unnamed: LED1.A, MINI_ITX_POWER_SUPPLY.8 (PWR_OK), POWER_BUTTON.1
unnamed: CONTROL_BOARD.8, CURRENT_SENSE.2
unnamed: MINI_ITX_POWER_SUPPLY.16 (PS_ON), POWER_BUTTON.2
unnamed: LED1.K (C), R1.1
unnamed: CONTROL_BOARD.9, HBRIDGE_CONTROL.5
unnamed: HBRIDGE_POWER_IN.3, MINI_ITX_POWER_SUPPLY.11 (12V)
unnamed: CUVETTE_PELT_OUT.1, HBRIDGE_A_OUT.1
unnamed: CUVETTE_PELT_OUT.2, HBRIDGE_A_OUT.2
unnamed: CCD_PELT_OUT.2, HBRIDGE_B_OUT.2
unnamed: CCD_PELT_OUT.1, HBRIDGE_B_OUT.1
unnamed: CONTROL_BOARD.7, HBRIDGE_CONTROL.4
unnamed: CONTROL_BOARD.5, HBRIDGE_CONTROL.3
unnamed: CONTROL_BOARD.3, HBRIDGE_CONTROL.2
unnamed: CURRENT_SENS_PWR.1, HBRIDGE_POWER_IN.2
unnamed: BOARD_POWER_OUT.1, CONTROL_BOARD.1, CURRENT_SENSE.3, CURRENT_SENS_PWR.2, LASER_RELAY_CONTROL.1, MINI_ITX_POWER_SUPPLY.4 (5V), MINI_ITX_POWER_SUPPLY.6 (5V), MINI_ITX_POWER_SUPPLY.21 (5V), MINI_ITX_POWER_SUPPLY.22 (5V), MINI_ITX_POWER_SUPPLY.23 (5V), RASPI_POWER_OUT.1 (VCC)

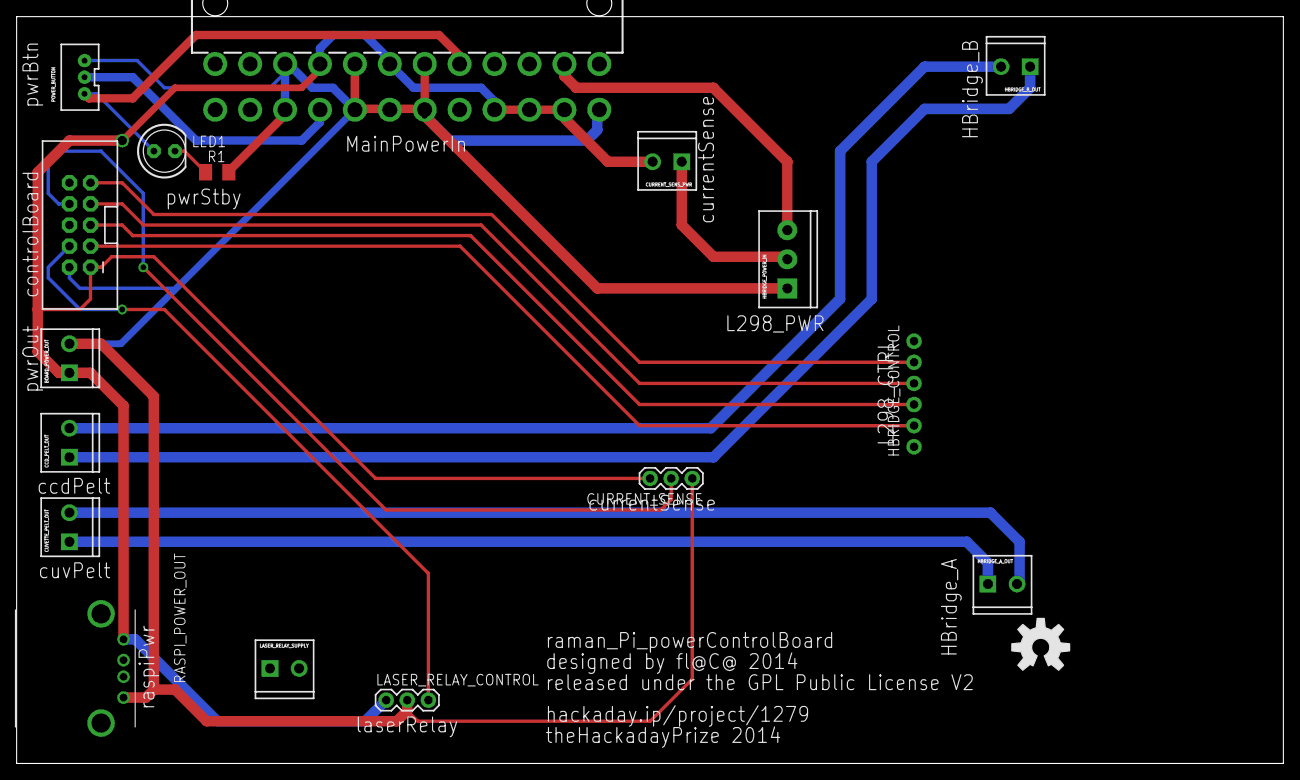
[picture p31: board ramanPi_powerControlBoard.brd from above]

Board: 2 copper layers, 152.4 x 89.8 mm, 19 parts (1 on the bottom side), 17 nets.

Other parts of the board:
U$1, U$2: OSHW-LOGO-L

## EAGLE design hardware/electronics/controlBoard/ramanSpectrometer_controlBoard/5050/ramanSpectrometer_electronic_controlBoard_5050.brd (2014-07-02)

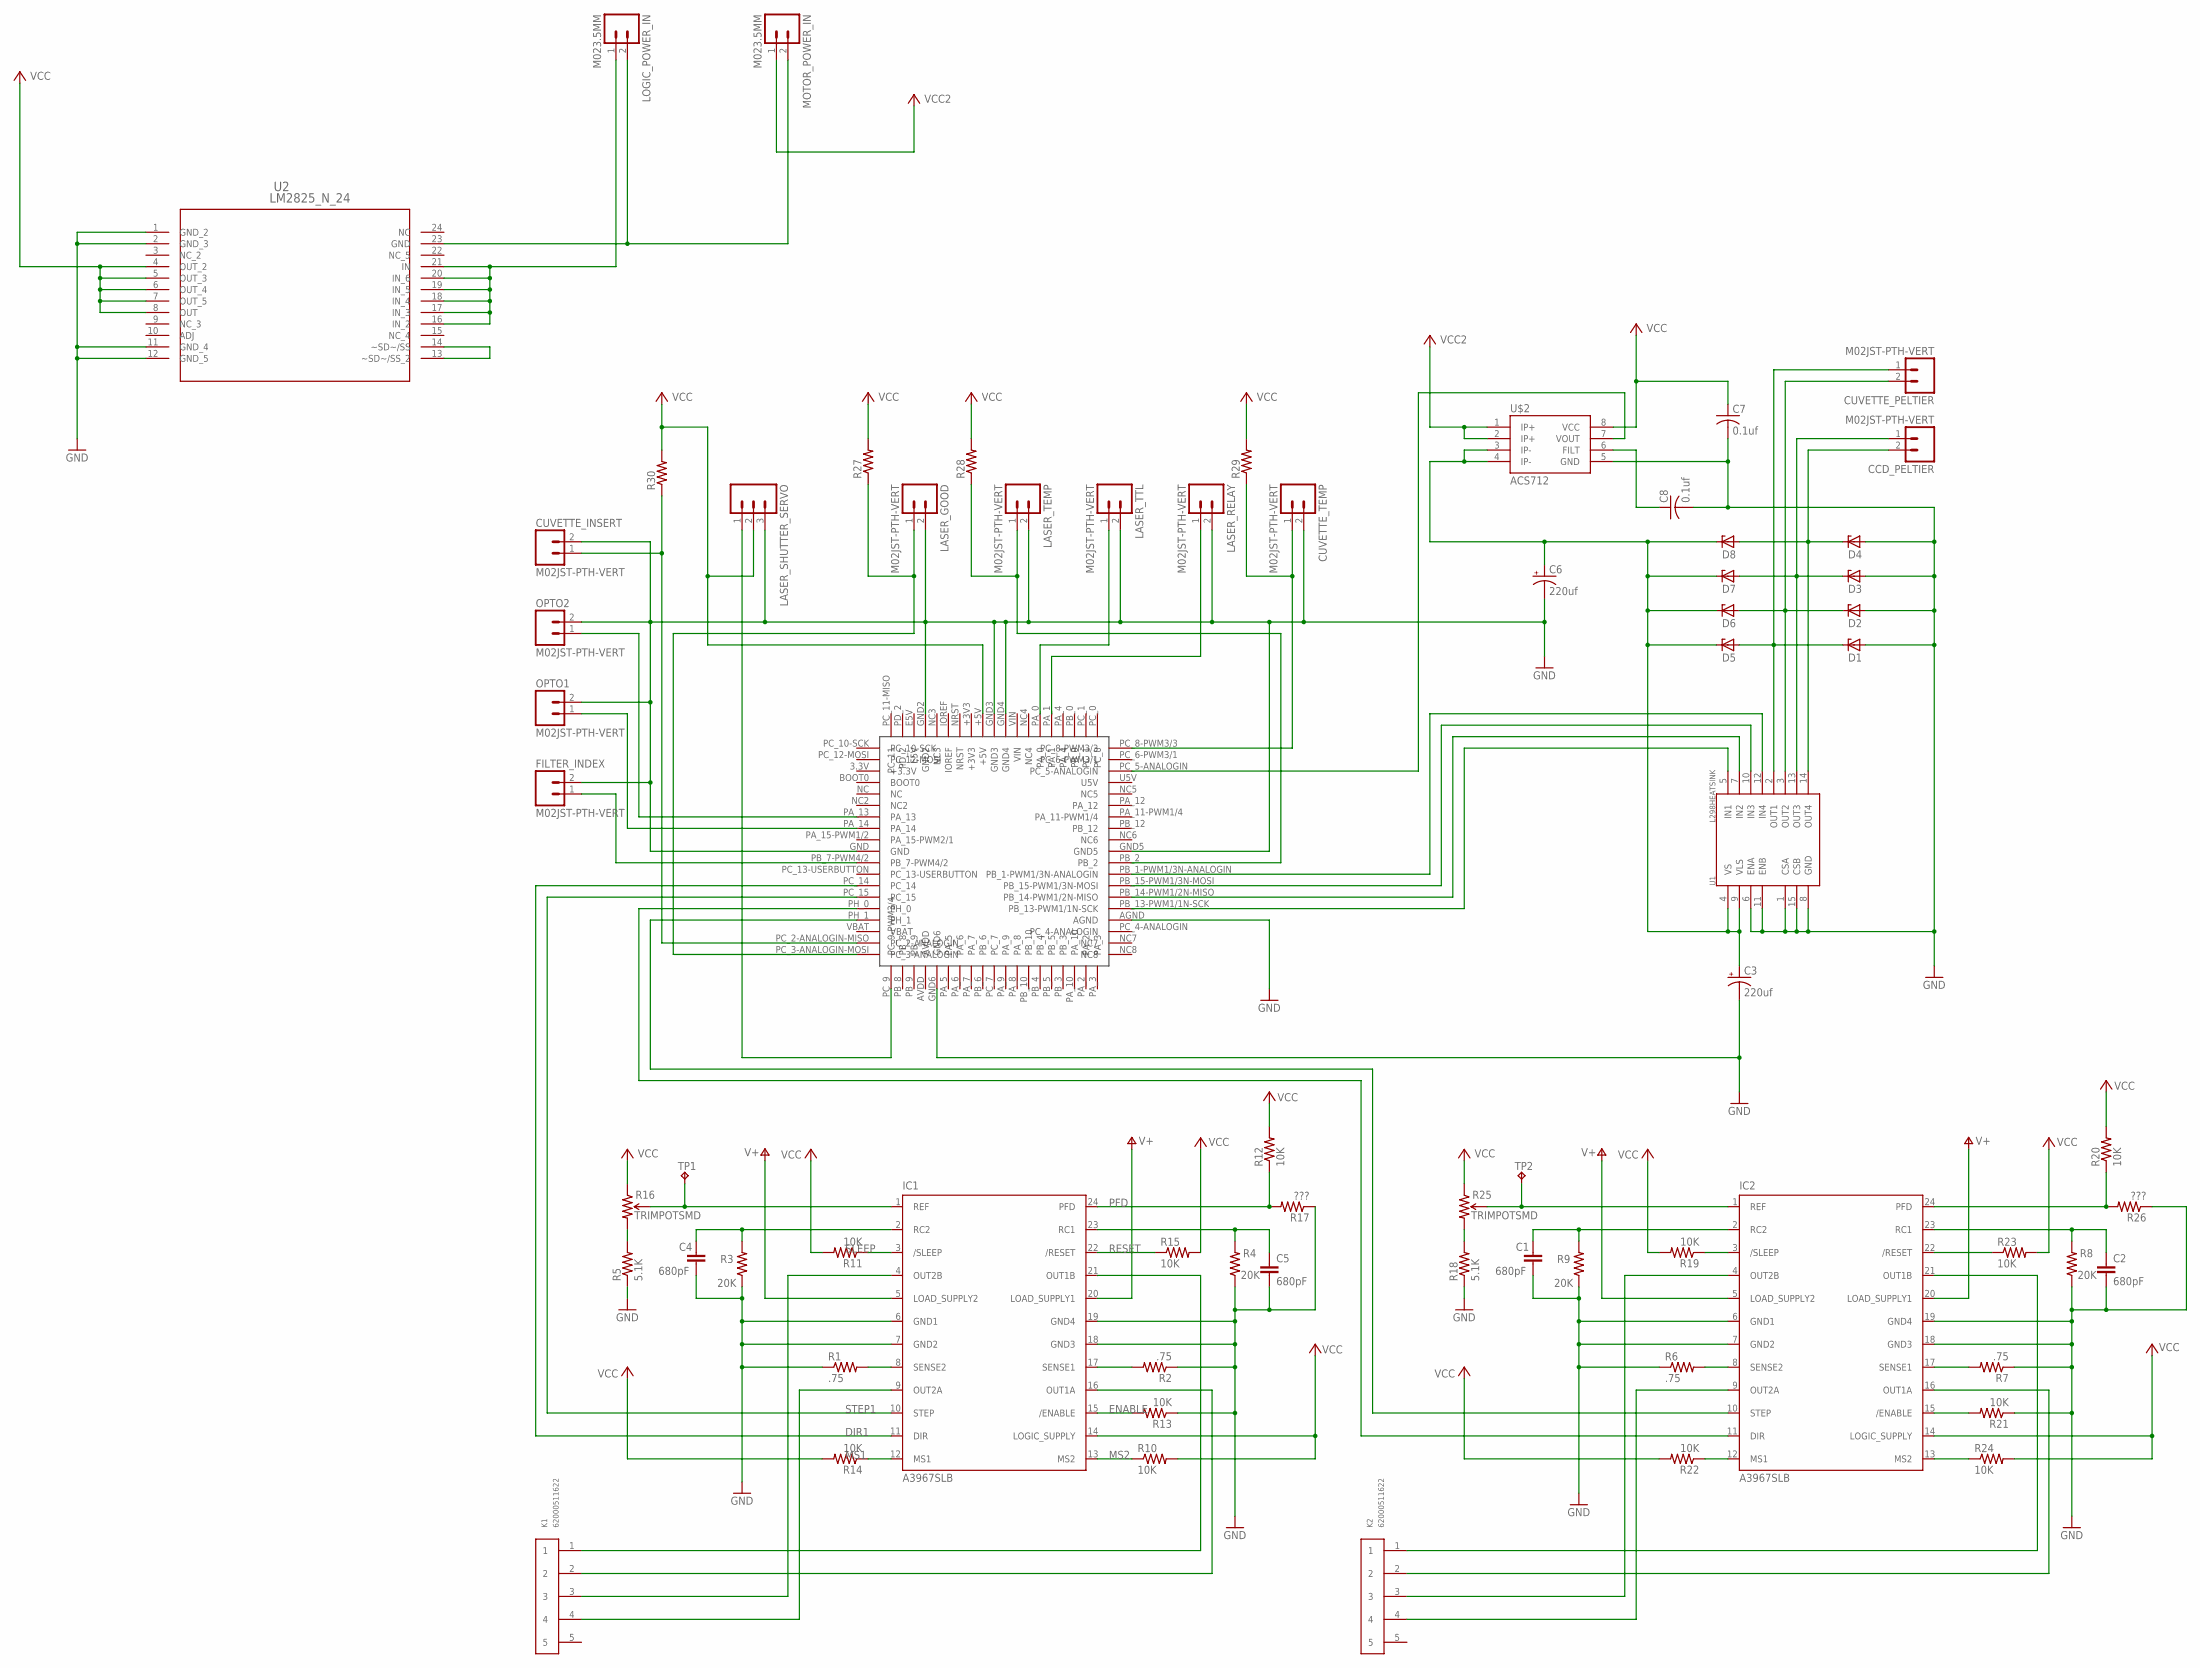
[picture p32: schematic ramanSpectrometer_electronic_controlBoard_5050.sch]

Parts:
C1, C2, C4, C5: 680pF; C0402
C3, C6: 220uf; PANASONIC_D
C7, C8: 0.1uf; C1206
CCD_PELTIER: M02JST-PTH-VERT; JST-2-PTH-VERT
CUVETTE_INSERT: M02JST-PTH-VERT; JST-2-PTH-VERT
CUVETTE_PELTIER: M02JST-PTH-VERT; JST-2-PTH-VERT
CUVETTE_TEMP: M02JST-PTH-VERT; JST-2-PTH-VERT
D1, D2, D3, D4, D5, D6, D7, D8: ZENER-DIODESMB; SMB
FILTER_INDEX: M02JST-PTH-VERT; JST-2-PTH-VERT
IC1, IC2: A3967SLB; SO24W
K1, K2: 62000511622
LASER_GOOD: M02JST-PTH-VERT; JST-2-PTH-VERT
LASER_RELAY: M02JST-PTH-VERT; JST-2-PTH-VERT
LASER_SHUTTER_SERVO: M03PTH; 1X03
LASER_TEMP: M02JST-PTH-VERT; JST-2-PTH-VERT
LASER_TTL: M02JST-PTH-VERT; JST-2-PTH-VERT
LOGIC_POWER_IN: M023.5MM; SCREWTERMINAL-3.5MM-2
MOTOR_POWER_IN: M023.5MM; SCREWTERMINAL-3.5MM-2
OPTO1, OPTO2: M02JST-PTH-VERT; JST-2-PTH-VERT
R1, R2, R6, R7: .75; R0805
R3, R4, R8, R9: 20K; C0402
R5, R18: 5.1K; C0402
R10, R11, R12, R13, R14, R15, R19, R20, R21, R22, R23, R24: 10K; C0402
R16, R25: TRIMPOTSMD; TRIMPOT-3MM
R17, R26: ???; C0402
R27, R28, R29, R30: R-US_M1206; M1206
TP1, TP2: TPPAD1-13; P1-13
U1: L298HEATSINK; MULTIWATT15_6400BGHEATSINK
U2: LM2825_N_24; NA24F
U$1: STNUCLEOF401RE; F401-RE
U$2: ACS712; SO08

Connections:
+3.3V: U$1.3.3V (+3.3V)
+5V: C7.1, IC1.14 (LOGIC_SUPPLY), IC2.14 (LOGIC_SUPPLY), LASER_SHUTTER_SERVO.2, MOTOR_POWER_IN.1, R10.2, R11.2, R19.2, R20.2, R22.2, R23.2, R24.2, R25.1 (CCW), R27.2, R28.2, R29.2, R30.2, U2.4 (OUT_2), U2.5 (OUT_3), U2.6 (OUT_4), U2.7 (OUT_5), U2.8 (OUT), U$1.+5V, U$2.8 (VCC)
AVDD: U$1.AVDD
DIR1: IC1.11 (DIR), U$1.PC_14
DIR2: IC2.11 (DIR), U$1.PH_0
E5V: U$1.E5V
ENABLE: IC1.15 (/ENABLE), R13.2
GND: C1.2, C2.2, C3.-, C4.2, C5.2, C6.-, C7.2, C8.2, CUVETTE_INSERT.2, CUVETTE_TEMP.2, D1.A, D2.A, D3.A, D4.A, FILTER_INDEX.2, IC1.6 (GND1), IC1.7 (GND2), IC1.18 (GND3), IC1.19 (GND4), IC2.6 (GND1), IC2.7 (GND2), IC2.18 (GND3), IC2.19 (GND4), LASER_GOOD.2, LASER_RELAY.2, LASER_SHUTTER_SERVO.3, LASER_TEMP.2, LASER_TTL.2, OPTO1.2, OPTO2.2, R1.1, R2.1, R3.1, R4.1, R5.1, R6.1, R7.1, R8.1, R9.1, R13.1, R17.1, R18.1, R21.1, R26.1, U1.1 (CSA), U1.6 (ENA), U1.8 (GND), U1.11 (ENB), U1.15 (CSB), U2.1 (GND_2), U2.2 (GND_3), U2.11 (GND_4), U2.12 (GND_5), U$1.AGND, U$1.GND, U$1.GND2, U$1.GND3, U$1.GND4, U$1.GND5, U$1.GND6, U$2.5 (GND)
MS1: IC1.12 (MS1), R14.1
MS2: IC1.13 (MS2), R10.1
unnamed: IC1.8 (SENSE2), R1.2
unnamed: IC2.24 (PFD), R20.1, R26.2
unnamed: IC1.17 (SENSE1), R2.2
unnamed: C2.1, IC2.23 (RC1), R8.2
unnamed: C4.1, IC1.2 (RC2), R3.2
unnamed: IC2.22 (/RESET), R23.1
unnamed: C5.1, IC1.23 (RC1), R4.2
unnamed: IC2.3 (/SLEEP), R19.1
unnamed: IC2.17 (SENSE1), R7.2
unnamed: R18.2, R25.3 (CW)
unnamed: R5.2, R16.3 (CW)
unnamed: IC1.1 (REF), R16.2 (WIPER), TP1.1
unnamed: CUVETTE_PELTIER.1, D1.C, D5.A, U1.2 (OUT1)
unnamed: CUVETTE_PELTIER.2, D2.C, D6.A, U1.3 (OUT2)
unnamed: CCD_PELTIER.1, D3.C, D7.A, U1.13 (OUT3)
unnamed: CCD_PELTIER.2, D4.C, D8.A, U1.14 (OUT4)
unnamed: U1.5 (IN1), U$1.PB_13-PWM1/1N-SCK
unnamed: U1.7 (IN2), U$1.PB_14-PWM1/2N-MISO
unnamed: U1.10 (IN3), U$1.PB_15-PWM1/3N-MOSI
unnamed: U1.12 (IN4), U$1.PB_1-PWM1/3N-ANALOG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
unnamed: C3.+, C6.+, D5.C, D6.C, D7.C, D8.C, U1.4 (VS), U1.9 (VLS), U$2.3 (IP-), U$2.4 (IP-)
unnamed: U$2.1 (IP+), U$2.2 (IP+)
unnamed: C8.1, U$2.6 (FILT)
unnamed: U$1.PC_5-ANALOGIN, U$2.7 (VOUT)
unnamed: CUVETTE_TEMP.1, R29.1, U$1.PC_8-PWM3/3
unnamed: LASER_RELAY.1, U$1.PA_1
unnamed: LASER_TTL.1, U$1.PA_0
unnamed: LASER_TEMP.1, R28.1, U$1.PB_2
unnamed: LASER_GOOD.1, R27.1, U$1.PC_3-ANALOGIN-MOSI (PC_3-ANALOGIN)
unnamed: CUVETTE_INSERT.1, R30.1, U$1.PC_2-ANALOGIN-MISO (PC_2-ANALOGIN)
unnamed: OPTO2.1, U$1.PA_13
unnamed: OPTO1.1, U$1.PA_14
unnamed: LOGIC_POWER_IN.2, MOTOR_POWER_IN.2, U2.23 (GND)
unnamed: IC2.15 (/ENABLE), R21.2
unnamed: LASER_SHUTTER_SERVO.1, U$1.PC_9 (PC_9-PWM3/4)
unnamed: U2.13 (~SD~/SS_2), U2.14 (~SD~/SS)
unnamed: LOGIC_POWER_IN.1, U2.16 (IN_2), U2.17 (IN_3), U2.18 (IN_4), U2.19 (IN_5), U2.20 (IN_6), U2.21 (IN)
unnamed: IC2.13 (MS2), R24.1
unnamed: IC2.1 (REF), R25.2 (WIPER), TP2.1
unnamed: IC2.12 (MS1), R22.1
unnamed: IC2.8 (SENSE2), R6.2
unnamed: C1.1, IC2.2 (RC2), R9.2
unnamed: IC2.9 (OUT2A), K2.4
unnamed: IC2.4 (OUT2B), K2.3
unnamed: IC1.4 (OUT2B), K1.3
unnamed: IC1.9 (OUT2A), K1.4
unnamed: IC1.16 (OUT1A), K1.2
unnamed: IC1.21 (OUT1B), K1.1
unnamed: FILTER_INDEX.1, U$1.PB_7-PWM4/2
NC6: U$1.NC6
OUT1A: IC2.16 (OUT1A), K2.2
OUT1B: IC2.21 (OUT1B), K2.1
PFD: IC1.24 (PFD), R12.1, R17.2
RESET: IC1.22 (/RESET), R15.1
SLEEP: IC1.3 (/SLEEP), R11.1
STEP1: IC1.10 (STEP), U$1.PC_15
STEP2: IC2.10 (STEP), U$1.PH_1
V+: IC1.5 (LOAD_SUPPLY2), IC1.20 (LOAD_SUPPLY1), IC2.5 (LOAD_SUPPLY2), IC2.20 (LOAD_SUPPLY1)
VBAT: U$1.VBAT
VCC: R12.2, R14.2, R15.2, R16.1 (CCW)


Board: 2 copper layers, 160.0 x 100.0 mm, 70 parts (0 on the bottom side), 65 nets.

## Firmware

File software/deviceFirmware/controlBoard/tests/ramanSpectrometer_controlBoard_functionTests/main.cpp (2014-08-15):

#include "mbed.h"
#include "DS18B20.h"
#include "OneWireDefs.h"

#define THERMOMETER DS18B20

#define     msg_cuvette_tray            0x10
#define     msg_cuvette_temp            0x11
#define     msg_cuvette_status          0x12
#define     msg_cuvette_tray_pos        0x13
#define     msg_cuvette_pelt_status     0x14
#define     msg_cuvette_stepper         0x15

#define     msg_filter_wheel            0x20
#define     msg_filter_pos              0x21

#define     msg_laser_temp              0x30
#define     msg_laser_power_status      0x31
#define     msg_laser_ttl_status        0x32
#define     msg_laser_good_status       0x33
#define     msg_laser_color             0x34
#define     msg_uv_index                0x35

#define     msg_ccd_pelt_status         0x40

#define     msg_shutter_servo_pos       0x50
#define     msg_shutter_status          0x51

#define     msg_board_ID                0x60
#define     msg_board_serial            0x61
#define     msg_board_status            0x62
#define     msg_board_time              0x63
#define     msg_board_model             0x64
#define     msg_board_version           0x65
#define     req_reboot                  0x66

#define     msg_ambient_temp            0x70
#define     req_baro                    0x71
#define     req_humidity                0x72

#define     cmd_cuvette                 0xA0
#define     tray_open                   0xA1
#define     tray_close                  0xA2
#define     cuvette_peltier             0xA3
#define     req_cuvette_status          0xA4
#define     req_cuvette_temp            0xA5
#define     req_cuvette_pelt_status     0xA6
#define     req_cuvette_tray_pos        0xA7

#define     cmd_filter_wheel            0xB0
#define     filter_select               0xB1
#define     filter_reset                0xB2
#define     req_filter_ID               0xB3
#define     req_filter_status           0xB4
#define     req_filter_count            0xB5
#define     req_filter_pos              0xB6

#define     cmd_laser                   0xC0
#define     laser_power                 0xC1
#define     laser_ttl                   0xC2
#define     req_laser_good_status       0xC3
#define     req_laser_color             0xC4
#define     req_laser_temp              0xC5
#define     req_uv_index                0xC6

#define     cmd_ccd_peltier             0xD0
#define     cmd_ccd_pelt_power          0xD1
#define     cmd_cuvette_peltier         0xD2
#define     cmd_cuvette_pelt_power      0xD3
#define     req_pelt_cool               0xD4
#define     req_pelt_heat               0xD5
#define     req_pelt_off                0xD6

#define     cmd_shutter_servo           0xE0
#define     shutter_open                0xE1
#define     shutter_close               0xE2
#define     shutter_deflect             0xE3
#define     shutter_alternate           0xE4
#define     req_shutter_state           0xE5
#define     req_shutter_status          0xE6

#define     packet_start                0xF0
#define     packet_ack                  0xF1
#define     packet_flag                 0xF2
#define     packet_end                  0xF3
#define     packet_err                  0xF4
#define     cmd_err                     0xF5
#define     req_err                     0xF6
#define     brd_err                     0xF7

#define     env_err                     0x80
#define     cuvette_err                 0x81
#define     laser_err                   0x82
#define     filter_err                  0x83
#define     ccd_pelt_err                0x84
#define     cuvette_pelt_err            0x85
#define     shutter_err                 0x86
#define     board_err                   0x87

DigitalIn button(USER_BUTTON);
DigitalOut grnLED(LED1);
DigitalOut cuvette_IN1(PC_14);
DigitalOut cuvette_IN2(PC_15);
DigitalOut cuvette_IN3(PH_0);
DigitalOut cuvette_IN4(PH_1);
DigitalOut filter_IN1(PA_4);
DigitalOut filter_IN2(PB_0);
DigitalOut filter_IN3(PC_1);
DigitalOut filter_IN4(PC_0);
PwmOut cuvettePeltA(PB_13); // in4
PwmOut cuvettePeltB(PB_14); // in3
PwmOut ccdPeltA(PB_1);      // in2
PwmOut ccdPeltB(PB_15);     // in1
AnalogIn peltCurrent(PC_5);

const int mDelay=1;
double temp;
int z;
int trayOpen;
THERMOMETER device(PC_8);
Serial raspi(USBTX, USBRX);

typedef union bytes {
    double d ;
    char c[8];
} bytes;

void printDoubleToHex(double d)
{
    bytes b;
    b.d = d;
    raspi.printf("%f -> %x %x %x %x %x %x %x %x\r\n", b.d, b.c[0], b.c[1], b.c[2], b.c[3], b.c[4], b.c[5], b.c[6], b.c[7]);
}

void printHexToDouble(char *arr)
{
    bytes b;
    for (int i=0; i<8; ++i)
        b.c[i] = arr[i];
    raspi.printf("received hex: %x %x %x %x %x %x %x %x \r\n", b.c[0], b.c[1], b.c[2], b.c[3], b.c[4], b.c[5], b.c[6], b.c[7]);
    raspi.printf("convert to: %f\r\n", b.d);
}

void readTemp(int deviceNum)
{
    temp = device.readTemperature(deviceNum);
    if (deviceNum == 0) {
//        raspi.printf("Cuvette Temperature: %f\r\n", temp);
//        const char begin[2]= {packet_flag, packet_start};
//        raspi.printf(begin);
        printDoubleToHex(temp);
//        const char stop[2]= {packet_flag, packet_end};
//        raspi.printf(stop);
    }
    if (deviceNum == 1) {
//        raspi.printf("Laser Emitter Temperature: %f\r\n", temp);
//        const char begin[2]= {packet_flag, packet_start};
//        raspi.printf(begin);
        printDoubleToHex(temp);
//        const char stop[2]= {packet_flag, packet_end};
//        raspi.printf(stop);
    }
//    raspi.printf("Device %d is %f",deviceNum, temp);
    wait(0.5);
}

int openTray()
{
    while (z < 500) {
        z++;
        grnLED = 1;
        wait_ms(1);
        cuvette_IN1 = 0;
        cuvette_IN2= 0;
        cuvette_IN3= 0;
        cuvette_IN4= 1;
        wait_ms(mDelay);

        cuvette_IN1= 0;
        cuvette_IN2= 0;
        cuvette_IN3= 1;
        cuvette_IN4= 1;
        wait_ms(mDelay);

        cuvette_IN1= 0;
        cuvette_IN2= 0;
        cuvette_IN3= 1;
        cuvette_IN4= 0;
        wait_ms(mDelay);

        cuvette_IN1= 0;
        cuvette_IN2= 1;
        cuvette_IN3= 1;
        cuvette_IN4= 0;
        wait_ms(mDelay);

        cuvette_IN1= 0;
        cuvette_IN2= 1;
        cuvette_IN3= 0;
        cuvette_IN4= 0;
        wait_ms(mDelay);

        cuvette_IN1= 1;
        cuvette_IN2= 1;
        cuvette_IN3= 0;
        cuvette_IN4= 0;
        wait_ms(mDelay);

        cuvette_IN1= 1;
        cuvette_IN2= 0;
        cuvette_IN3= 0;
        cuvette_IN4= 0;
        wait_ms(mDelay);

        cuvette_IN1= 1;
        cuvette_IN2= 0;
        cuvette_IN3= 0;
        cuvette_IN4= 1;
        wait_ms(mDelay);

        cuvette_IN1= 0;
        cuvette_IN2= 0;
        cuvette_IN3= 0;
        cuvette_IN4= 0;
    }
    trayOpen = 1;
    z = 0;
    return(0);
}

int closeTray()
{
    while (z < 500) {
        z++;
        grnLED = 1;
        wait_ms(1);
        cuvette_IN1= 1;
        cuvette_IN2= 0;
        cuvette_IN3= 0;
        cuvette_IN4= 1;
        wait_ms(mDelay);

        cuvette_IN1= 1;
        cuvette_IN2= 0;
        cuvette_IN3= 0;
        cuvette_IN4= 0;
        wait_ms(mDelay);

        cuvette_IN1= 1;
        cuvette_IN2= 1;
        cuvette_IN3= 0;
        cuvette_IN4= 0;
        wait_ms(mDelay);

        cuvette_IN1= 0;
        cuvette_IN2= 1;
        cuvette_IN3= 0;
        cuvette_IN4= 0;
        wait_ms(mDelay);

        cuvette_IN1= 0;
        cuvette_IN2= 1;
        cuvette_IN3= 1;
        cuvette_IN4= 0;
        wait_ms(mDelay);

        cuvette_IN1= 0;
        cuvette_IN2= 0;
        cuvette_IN3= 1;
        cuvette_IN4= 0;
        wait_ms(mDelay);

        cuvette_IN1= 0;
        cuvette_IN2= 0;
        cuvette_IN3= 1;
        cuvette_IN4= 1;
        wait_ms(mDelay);

        cuvette_IN1= 0;
        cuvette_IN2= 0;
        cuvette_IN3= 0;
        cuvette_IN4= 1;
        wait_ms(mDelay);

        cuvette_IN1= 0;
        cuvette_IN2= 0;
        cuvette_IN3= 0;
        cuvette_IN4= 0;
    }
    trayOpen = 0;
    z = 0;
    return(0);
}

int filterForward()
{
    while (z < 500) {
        z++;
        grnLED = 1;
        wait_ms(1);
        filter_IN1 = 0;
        filter_IN2= 0;
        filter_IN3= 0;
        filter_IN4= 1;
        wait_ms(mDelay);

        filter_IN1= 0;
        filter_IN2= 0;
        filter_IN3= 1;
        filter_IN4= 1;
        wait_ms(mDelay);

        filter_IN1= 0;
        filter_IN2= 0;
        filter_IN3= 1;
        filter_IN4= 0;
        wait_ms(mDelay);

        filter_IN1= 0;
        filter_IN2= 1;
        filter_IN3= 1;
        filter_IN4= 0;
        wait_ms(mDelay);

        filter_IN1= 0;
        filter_IN2= 1;
        filter_IN3= 0;
        filter_IN4= 0;
        wait_ms(mDelay);

        filter_IN1= 1;
        filter_IN2= 1;
        filter_IN3= 0;
        filter_IN4= 0;
        wait_ms(mDelay);

        filter_IN1= 1;
        filter_IN2= 0;
        filter_IN3= 0;
        filter_IN4= 0;
        wait_ms(mDelay);

        filter_IN1= 1;
        filter_IN2= 0;
        filter_IN3= 0;
        filter_IN4= 1;
        wait_ms(mDelay);

        filter_IN1= 0;
        filter_IN2= 0;
        filter_IN3= 0;
        filter_IN4= 0;
    }
    z = 0;
    return(0);
}
int filterBack()
{
    while (z < 500) {
        z++;
        grnLED = 0;
        wait_ms(1);
        filter_IN1= 1;
        filter_IN2= 0;
        filter_IN3= 0;
        filter_IN4= 1;
        wait_ms(mDelay);

        filter_IN1= 1;
        filter_IN2= 0;
        filter_IN3= 0;
        filter_IN4= 0;
        wait_ms(mDelay);

        filter_IN1= 1;
        filter_IN2= 1;
        filter_IN3= 0;
        filter_IN4= 0;
        wait_ms(mDelay);

        filter_IN1= 0;
        filter_IN2= 1;
        filter_IN3= 0;
        filter_IN4= 0;
        wait_ms(mDelay);

        filter_IN1= 0;
        filter_IN2= 1;
        filter_IN3= 1;
        filter_IN4= 0;
        wait_ms(mDelay);

        filter_IN1= 0;
        filter_IN2= 0;
        filter_IN3= 1;
        filter_IN4= 0;
        wait_ms(mDelay);

        filter_IN1= 0;
        filter_IN2= 0;
        filter_IN3= 1;
        filter_IN4= 1;
        wait_ms(mDelay);

        filter_IN1= 0;
        filter_IN2= 0;
        filter_IN3= 0;
        filter_IN4= 1;
        wait_ms(mDelay);

        filter_IN1= 0;
        filter_IN2= 0;
        filter_IN3= 0;
        filter_IN4= 0;
    }
    z = 0;
    return(0);
}

int cuvettePeltCycle(){
    cuvettePeltA = 0;
    cuvettePeltB = 0;
    wait(3);
    cuvettePeltA = 1;
    cuvettePeltB = 1;
    wait(3);
    cuvettePeltA = 1;
    cuvettePeltB = 0;
    wait(3);
    cuvettePeltA = 0;
    cuvettePeltB = 1;
    wait(3);
    cuvettePeltA = 0;
    cuvettePeltB = 0;
    return 0;
}
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

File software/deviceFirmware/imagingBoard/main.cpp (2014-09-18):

#include "mbed.h"

//  ***   BE SURE TO TEST BEFORE AND AFTER FOR 'IDLING'... CLEAR THE CCD EVERY OTHER FRAME TO TRY AND ELIMINATE NOISE BUILDUP
//From http://www.ing.iac.es/~docs/ins/das/ins-das-29/integration.html
//"Idling" vs. integrating
//Charge from light leaks and thermal noise builds up on the detector between observations. If this charge is integrated by the detector, it may not be completely
//cleared away by the clear cycle of the next observation. In that case, the observation will be contaminated by extra counts. (Often, this appears as a ramp in the
//background leading up to a saturated region in the low-numbered rows.)
//To avoid this problem, the detector is made to clear itself continuously between observations. This is called "idling", and is reported as such on the mimic.

PwmOut masterClock(PB_4);
PwmOut shiftGate(PB_8);
InterruptIn shiftGate_int(PC_6);
DigitalOut ICG(PB_3);
AnalogIn imageIn(A0);
DigitalOut LED(LED1);
DigitalOut illuminator(PA_8);
DigitalOut blueLED(PB_5);
DigitalOut redLED(PB_10);
Serial raspi(USBTX, USBRX);

/*
int masterFreq_period       = 20;    //microseconds
int masterFreq_width        = 10;    //microseconds
int shiftGate_period        = 66;    //microseconds
int shiftGate_width         = 33;    //microseconds
*/

float firmwareVersion = 0.2;


int masterFreq_period       = 2;    //microseconds
int masterFreq_width        = 1;    //microseconds
int shiftGate_period        = 8;    //microseconds
int shiftGate_width         = 4;    //microseconds

int none        = 0;
int veryLow     = 10;
int low         = 100;
int mediumLow   = 1000;
int medium      = 100000;
int high        = 5000000;
int veryHigh    = 10000000;

double imageData;
int sensitivity;
int pixelTotal              = 3694;
int leadingDummyElements    = 16;
int leadShieldedElements    = 13;
int headerElements          = 3;
const int signalElements    = 3648;
int trailingDummyElements   = 14;
int pixelCount;
int readOutTrigger;
int state;

#define readOut_Begin               1
#define readOut_ACTIVE              2
#define readOut_LeadingDummy        3
#define readOut_LeadingShielded     4
#define readOut_headerElements      5
#define readOut_signalElements      6
#define readOut_trailingDummy       7
#define readOut_integrationTime     8
#define readOut_IDLE                9
#define readOut_Finish              0

#define MV(x) ((0xFFF*x)/3300)

double pixelValue[signalElements] = { 0 };

void error()
{
    while(1) {
        LED = !LED;
        wait(0.5);
    }
}
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

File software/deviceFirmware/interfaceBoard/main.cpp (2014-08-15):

#include "stdio.h"
#include "mbed.h"
#include "SPI_TFT_ILI9341.h"
#include "string"
#include "Arial12x12.h"
#include "Arial24x23.h"
#include "Arial28x28.h"
#include "font_big.h"
#include "MPR121.h"

I2C i2c(PB_9, PB_8);
InterruptIn irq(PC_8);
MPR121 touch_pad(i2c, irq, MPR121::ADDR_VSS);

extern unsigned char p1[];  // the mbed logo graphic
DigitalOut LCD_LED(D7);
DigitalOut led1(LED1);

SPI_TFT_ILI9341 TFT(D11, D12, D13, D8, D9, D10,"TFT"); // mosi, miso, sclk, cs, reset, dc

Serial raspi(USBTX, USBRX);

int splashScreen()
{
    double s;
    int i;

    TFT.set_orientation(1);
    TFT.background(Black);
    TFT.foreground(White);
    TFT.cls();

    TFT.set_orientation(0);
    TFT.background(Black);
    TFT.cls();

    TFT.set_orientation(1);
    for (i=0; i<320; i++) {
        s =40 * sin((long double) i / 10 );
        TFT.pixel(i+s,180 + (int)s+(s-i) ,Red);
    }

    for (i=0; i<320; i++) {
        s =40 * sin((long double) i / 10 );
        TFT.pixel(i,180 + (int)s+(s-i) ,Green);
    }

    for (i=0; i<320; i++) {
        s =40 * sin((long double) i / 10 );
        TFT.pixel(i-s,180 + (int)s+(s-i) ,Blue);
    }
    TFT.rect(0,0,320,240,Blue);
    TFT.set_font((unsigned char*) Neu42x35);
    TFT.locate(20,70);
    TFT.printf("meridian"); 
    TFT.locate(110,100);
    TFT.printf("Scientific");
    TFT.set_font((unsigned char*) Arial24x23);
    TFT.locate(30,140);
    TFT.printf("ramanSpectrometer");
    TFT.set_font((unsigned char*) Arial12x12);
    TFT.locate(160,165);
    printf("version0.1a (2014)");
    TFT.foreground(DarkGrey);
    TFT.locate(5,225);
    printf("http://www.meridian-scientific.com");
    return 0;
}
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

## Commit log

2014-05-29 Added Files
    Added all files from original location
    [Letters.dxf, Write.scad, arrow.scad, electronic_lcdDisplay.scad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]
2014-05-29 Mirror mount adjustment bracket
    Fixed and updated bracket sizes and recompiled stl files...
    [opticsMount_mirror_TopAndBottom.scad, opticsMount_mirror_TopAndBottom.stl, opticsMount_mirror_top.scad]
2014-05-29 Recompiled .stl files after fixing dimensions
    Mirror micro adjustment bracket needed some size adjustments.. The
    mirror main mount needed updating to the .stl file as well.
    [opticsMount_mirrorAssembly_rear.stl, opticsMount_mirror_top.stl]
2014-05-29 Added keys to objective lens mount for orientation
    Helps orient the top and bottom and lessen likelihood of the mount to
    move, etc..
    [opticsMount_objectiveLens_TopAndBottom.stl, opticsMount_objectiveLens_bottom.scad, opticsMount_objectiveLens_bottom.stl, opticsMount_objectiveLens_top.scad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]
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2014-05-30 Fixed bug that caused error in stl rendering
    The radius listed after height in the cylinders made it error while
    trying to print.. fixed them all.
    [filterMount_532nm_Pass_TopAndBottom.stl, filterMount_532nm_Pass_bottom.scad, filterMount_532nm_Pass_bottom.stl, filterMount_532nm_Pass_top.scad]
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2014-05-30 Updated 532nmPass Mount
    Modified to adjust the filter thickness..the mirror was a little wobbly
    inside the mount..this should tighten up the tolerances.. Also deleted
    the retired files...
    Other files are from rendering for the project log...
    [filterMount_532nm_Pass_TopAndBottom.stl, filterMount_532nm_Pass_bottom.scad, filterMount_532nm_Pass_bottom.stl, filterMount_532nm_Pass_bottom_retired.scad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]
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2014-06-05 updated controlBoard tray and the display trim
    Updated the controlBoard tray to accommodate the full pcb, which now
    just slides right into the mount nicely...
    Completely redesigned the display mechanical tray and the faceplace to
    accommodate the new color TFT display and a capacitive backlit touch
    panel that'll be built from scratch..
    [electronic_lcdDisplay_retired.scad, electronic_tftDisplay.scad, mechanical_tray_controlBoard.scad, mechanical_tray_controlBoard.stl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]
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2014-06-06 redesigned the display drive tray and faceplate
    total redesign for the tft display...
    [trim_tftFaceplate_driveTray.scad, trim_tftFaceplate_driveTray.stl, trim_tftFaceplate_facia.scad, trim_tftFaceplate_facia.stl]
2014-06-09 beginMajorOverhaul
    Addition of new objects to replace current system..
    [combined_completeSystem.scad, combined_mechanical_device_laserShutter.scad, combined_structural_mount_laser.scad, electronic_object_laser_emitter.scad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]
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2014-06-10 update name and redesigned objects
    redesigned laser emitter and shutter for better aesthetics and
    functionality
    [combined_completeSystem.scad, electronic_mount_laser_bottom.scad, electronic_mount_laser_bottom.stl, electronic_mount_laser_top.scad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]
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2014-06-10 fixed mirror mount
    errors in printing- resolved
    [combined_completeSystem.scad, combined_electronic_mount_laser.scad, combined_optics_module_surfaceMirror.scad]
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2014-06-11 created 532nmPassFilterMount
    Need to fix errors for printing...
    [optics_module_filter_532nmPass_bottom.scad, optics_module_filter_532nmPass_bottom.stl, optics_module_filter_532nmPass_top.scad, optics_module_filter_532nmPass_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]
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2014-07-23 fixing errors in objective lens mount
    [optics_module_objectiveLens_bottom.scad, optics_module_objectiveLens_bottom.stl, optics_module_objectiveLens_test.stl, optics_module_surfaceMirror_bottom.stl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]
2014-07-23 fixed minor errors and new tests
    minor errors in mirror mount
    uploaded new firmware tests and python code
    [optics_module_surfaceMirror_bottom.scad, optics_module_surfaceMirror_bottom.stl, optics_module_surfaceMirror_top.scad, optics_module_surfaceMirror_top.stl]
2014-07-29 fixed objectiveLensMount
    Made the upper and lower pieces more printable by ordering the unions,
    etc. properly...
    [objectiveMount_TEST.stl, optics_module_objectiveLens_bottom.scad, optics_module_objectiveLens_bottom.stl, optics_module_objectiveLens_test.scad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]
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2014-08-01 Added screw paths to mirror mount, added/modified web pix
    Added screw paths to mirror mount to allow for clearance of screws when
    assembling... Need to add adjustment screws and grommet groove as well.
    [mechanical_device_filterSelectorAssembly.scad, mechanical_device_filterSelectorAssembly.stl, optics_module_surfaceMirror_bottom.scad, optics_module_surfaceMirr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]
2014-08-02 Fixed Filter Wheel Assembly
    Fixed some errors that were preventing it from printing properly..
    The main body now prints..
    [mechanical_device_filterSelectorAssembly_back.scad, mechanical_device_filterSelectorAssembly_back.stl, mechanical_device_filterSelectorAssembly_front.scad, mec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]
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2014-08-11 Fixed display and keypad mount
    Angled it at a 45deg angle for mounting to the front of the case..
    Added some pics for ccd testing..
    [trim_tftFaceplate_keypad-display.scad, trim_tftFaceplate_keypad-display.stl]
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2014-08-16 fixed optics_module_testStand_lightMount
    Added lens mount for collimating lens testing
    [optics_module_testStand.scad, optics_module_testStand_lightMountFrontWithLens.stl, optics_module_testStand_lightMountTopLens.stl]
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2014-08-26 designRefresh for Spectrometer module
    Completely redesigning the geometry... when you change the angle of a
    mirror, or grating, the rest of the positions for other objects are
    automatically calculated
    [optics_module_spectrometer_v02.scad]
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2014-08-29 updatedConcaveMirrorTestAndCreatedTestStandV2
    made updates to concave mirror reflectance test
    created new test stand with fixed geometry
    [optics_module_testStand_V2.scad, optics_module_testStand_V2.stl, optics_module_test_concaveMirrorReflectance.scad, optics_module_test_flatMirrorReflectance.scad]
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2014-09-09 fixed top cover and added light baffles
    Fixed inside cylinder for top cover to make it fit into hole..
    Added light baffles for inside spectrometer.
    [optics_module_spectrometer_v04.scad, optics_module_spectrometer_v04_topCover.stl]
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2014-09-17 fixed laser test stand - dgmount
    Made flange mount more substantial
    corrected size for DG Mount base
    [optics_module_spectrometer_v04_DGMount.stl, optics_module_testStand.scad, optics_module_testStand_laserWflange.stl]
2014-09-19 updated filter wheel and cover plates
    Fixed mounts in filter wheel for 532nm and 550nm edge filters and
    created mounting plates
    [mechanical_device_filterSelectorAssembly_522nmSP_cover.stl, mechanical_device_filterSelectorAssembly_550nmSP_cover.stl, mechanical_device_filterSelectorAssembl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]
2014-09-19 updated beam splitter assembly
    Added access port cover
    Added beam splitter mount
    Fixed center hub and cross beam path
    [optics_module_beamSplitter_accessPortCover.stl, optics_module_beamSplitter_bottom.scad, optics_module_beamSplitter_bottom.stl, optics_module_beamSplitter_split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]
2014-09-19 updated splitter and filter
    made splitter mount thicker
    made more room for 550nm filter
    modified hub to allow for clearance
    [mechanical_device_filterSelectorAssembly_550nmSP_cover.stl, mechanical_device_filterSelectorAssembly_filterWheel.scad, mechanical_device_filterSelectorAssembly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]
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2014-09-20 minor adjustment to filterSelctor Assembly
    Made more clearance for filter mounts to move
    [mechanical_device_filterSelectorAssembly_back.scad, mechanical_device_filterSelectorAssembly_back.stl, mechanical_device_filterSelectorAssembly_front.scad, mec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]
2014-09-20 minor adjustments to filter selector assembly
    minor clearance issues fixed
    [mechanical_device_filterSelectorAssembly_back.scad, mechanical_device_filterSelectorAssembly_back.stl, mechanical_device_filterSelectorAssembly_front.scad, mec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]
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2014-09-22 updated objective lens mount
    fixed dimensions for object lens to better fit
    adjusted mounting screw holes to allow for shorter screws
    removed slits on sides to better block ambient and incidental light -
    also stronger structurally
    [optics_module_objectiveLens_bottom.scad, optics_module_objectiveLens_bottom.stl, optics_module_objectiveLens_top.scad, optics_module_objectiveLens_top.stl]
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2014-10-08 fixed silkscreen for imagingBoard
    ccdTemp label said laserTemp - fixed, now says ccdTemp
    [ramanPi_imagingBoard.GTO, ramanPi_imagingBoard.brd]
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2014-10-09 imagingBoard_ccd fixes
    updated board layout and schematic
    decoupling capacitors added
    ground planes and routing redone
    dimensions for screw holes fixed
    [ramanPi_imagingBoard_ccdBoard.GBL, ramanPi_imagingBoard_ccdBoard.GBO, ramanPi_imagingBoard_ccdBoard.GBS, ramanPi_imagingBoard_ccdBoard.GTL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]
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2014-10-24 new cuvette tray assembly
    fixed some minor details and added a thicker door
    [mechanical_device_cuvetteTrayAssembly.scad, mechanical_device_cuvetteTrayAssembly.stl]
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

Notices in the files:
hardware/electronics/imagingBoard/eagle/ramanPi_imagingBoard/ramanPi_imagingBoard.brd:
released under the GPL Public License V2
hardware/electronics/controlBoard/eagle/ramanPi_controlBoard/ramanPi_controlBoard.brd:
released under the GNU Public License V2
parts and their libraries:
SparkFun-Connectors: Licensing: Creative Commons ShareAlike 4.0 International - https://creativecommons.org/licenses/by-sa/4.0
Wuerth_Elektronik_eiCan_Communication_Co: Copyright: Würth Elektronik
